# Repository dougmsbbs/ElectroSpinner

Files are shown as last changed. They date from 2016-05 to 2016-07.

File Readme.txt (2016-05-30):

   The Whirl-A-Rama is a open source electrospinning machine designed for anyone to be able to reproduce. It is made from commonly available materials at low cost.
   It is an entry into the 2016 HackaDay prize contest. You can view it here: https://hackaday.io/project/10599-electrospinning-machine
   For an introduction to electrospinning, this is a good start: https://en.wikipedia.org/wiki/Electrospinning More links are available from the HackaDay project page listed above.
   Any questions or comments, my email address is dougmsbbs@hotmail.com
   NOTE: ALL of the files associated with this project are in a state of flux right now. The project is being actively developed and things not only 'might' change, they 'will' change!

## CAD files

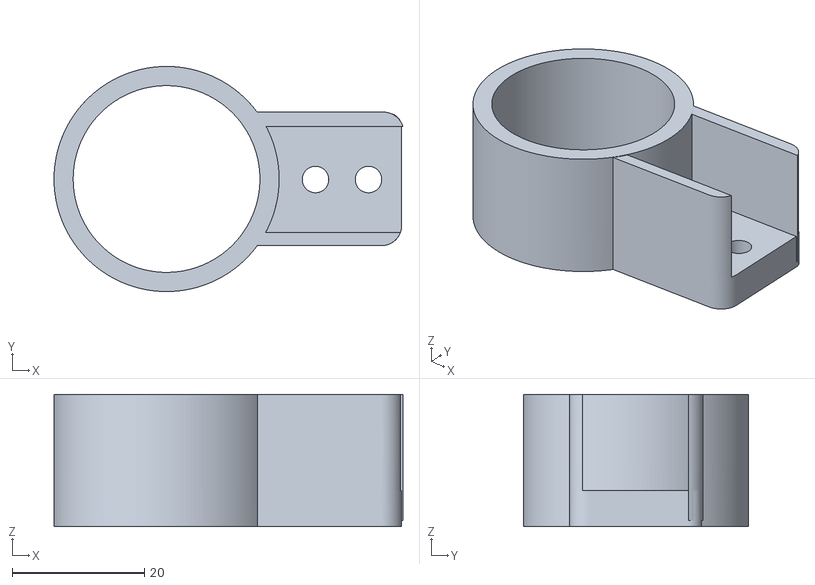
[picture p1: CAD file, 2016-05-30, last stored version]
Electrospinner/SwingHinge.stl
52.7 x 34.0 x 20.0

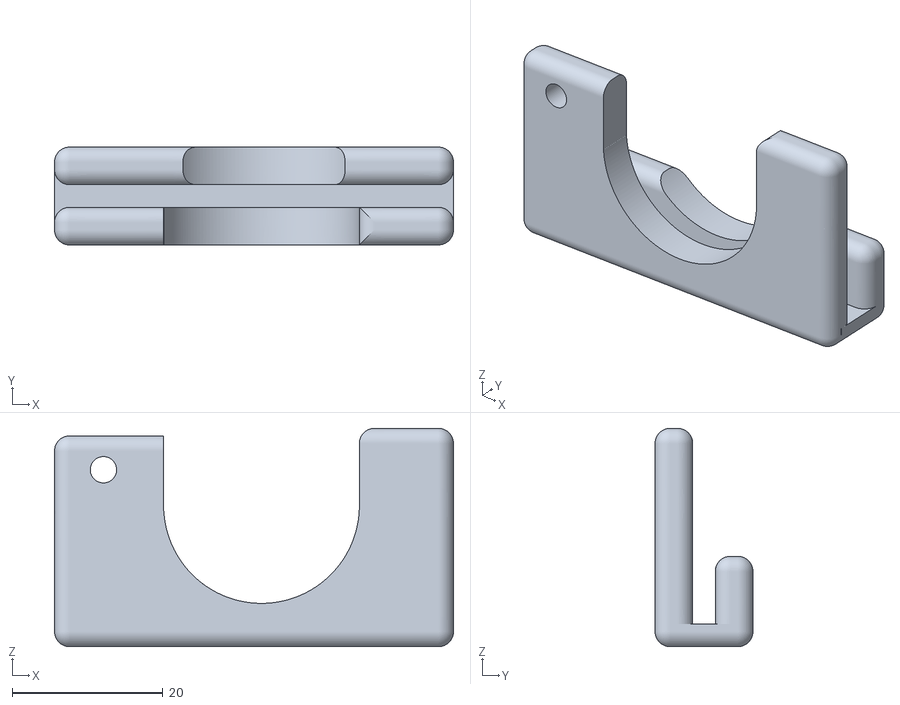
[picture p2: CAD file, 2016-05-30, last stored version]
Syringe/PlungerMountCap.stl
53.0 x 13.0 x 29.0

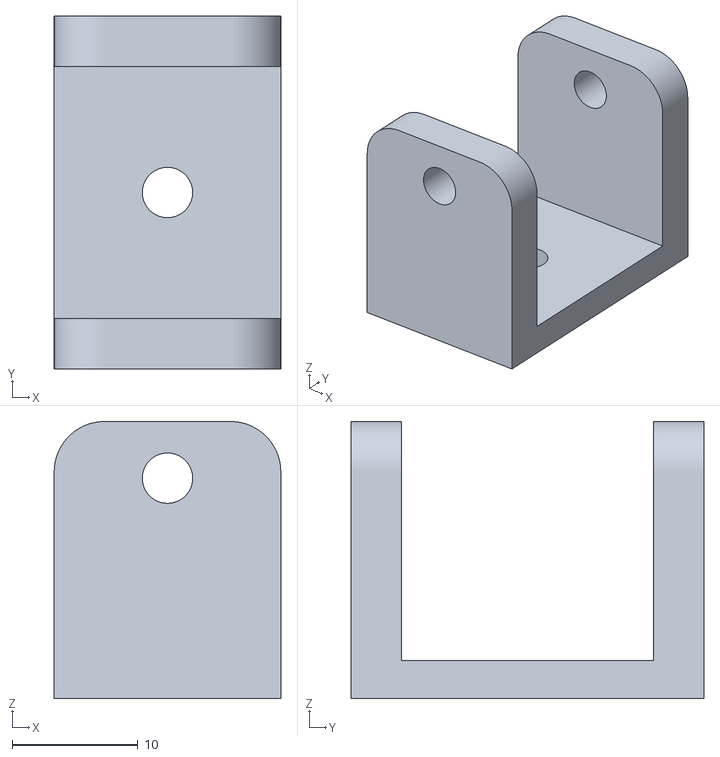
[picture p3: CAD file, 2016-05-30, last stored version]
Electrospinner/BottomIdlerBracket.stl
18.0 x 28.0 x 22.0

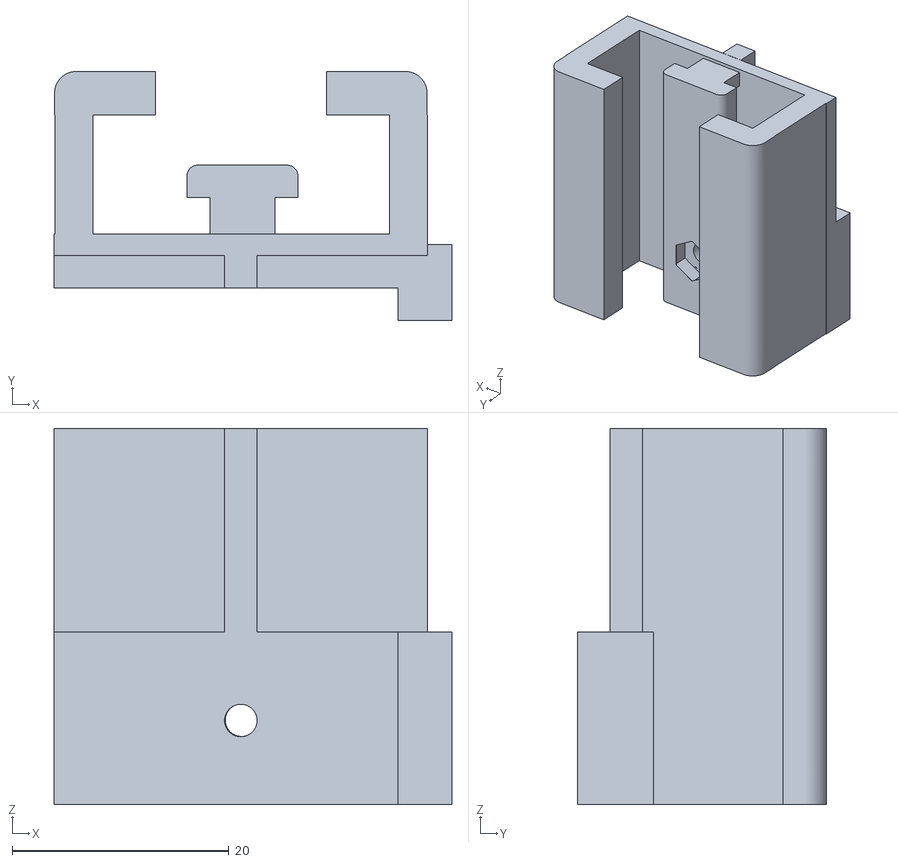
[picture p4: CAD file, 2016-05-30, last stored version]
Syringe/PlungerCarriageSlide.stl
36.8 x 23.0 x 34.7

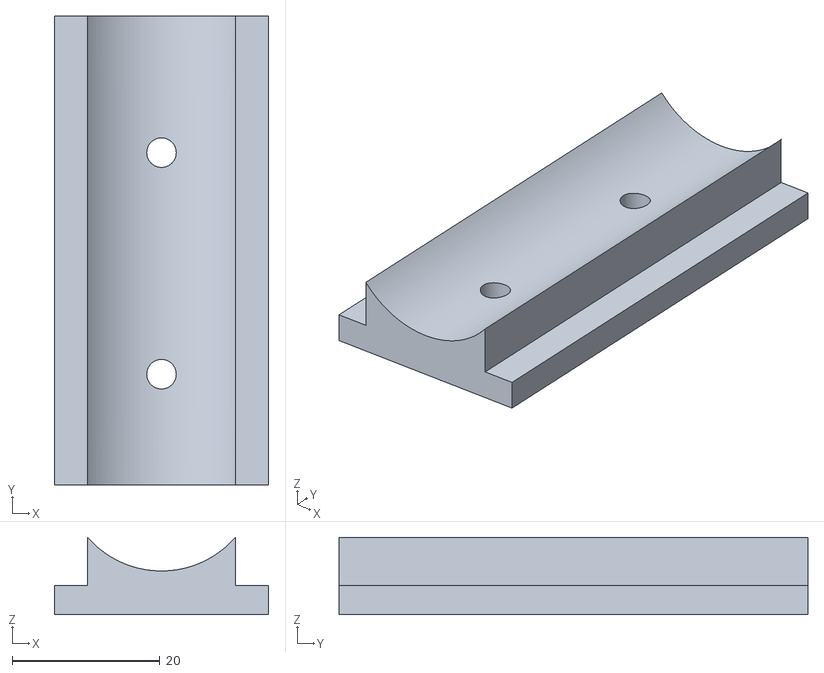
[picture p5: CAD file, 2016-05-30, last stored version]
Electrospinner/SideCoverBracket.stl
29.0 x 63.5 x 10.5

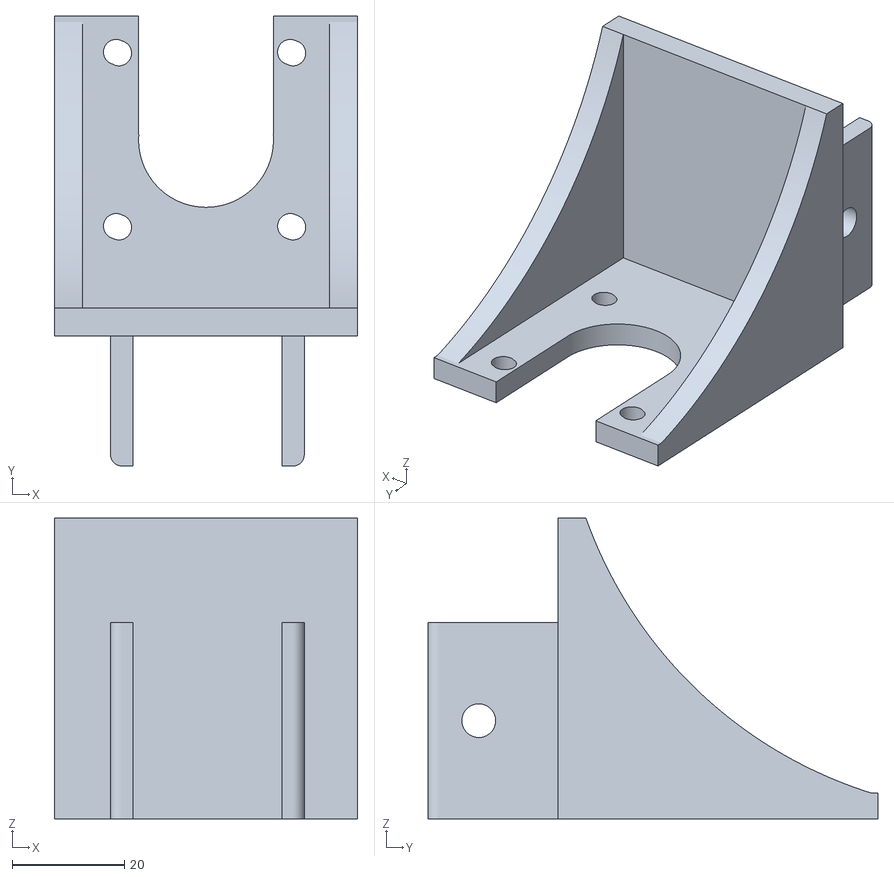
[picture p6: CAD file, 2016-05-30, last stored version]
Syringe/SyringeMotorMount.stl
54.0 x 80.1 x 53.6

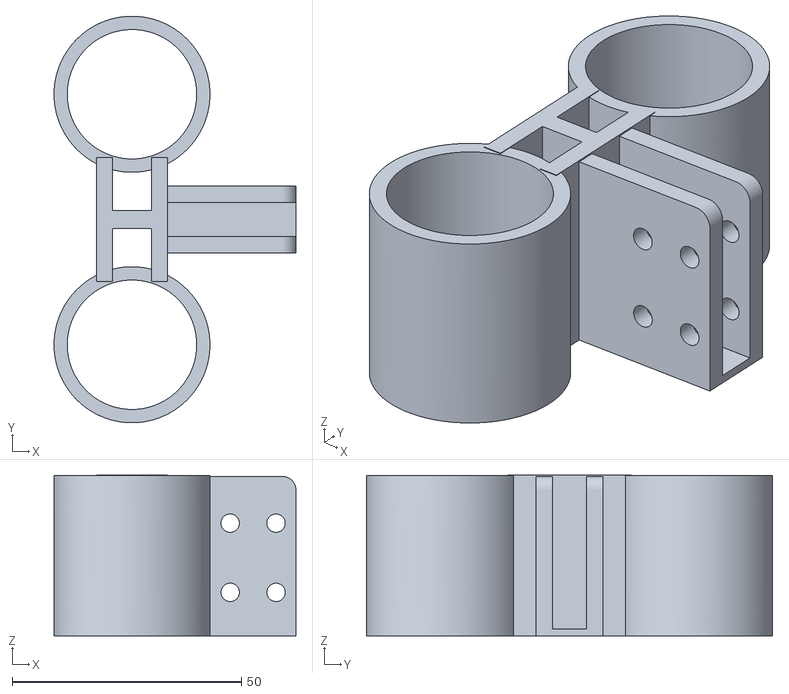
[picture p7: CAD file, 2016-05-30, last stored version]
Electrospinner/DoubleShaftCollar.stl
52.8 x 88.6 x 35.0

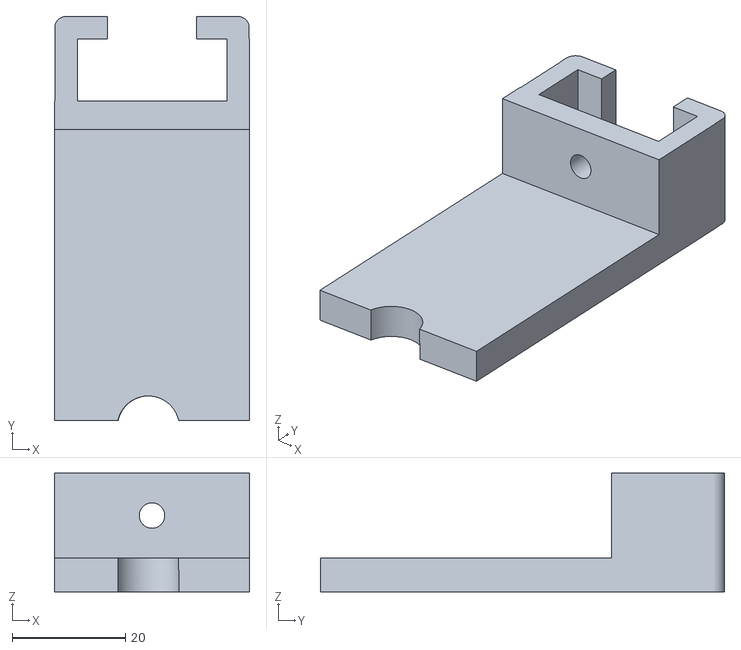
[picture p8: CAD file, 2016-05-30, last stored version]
Syringe/SyringeTipMount.stl
34.5 x 71.5 x 21.0

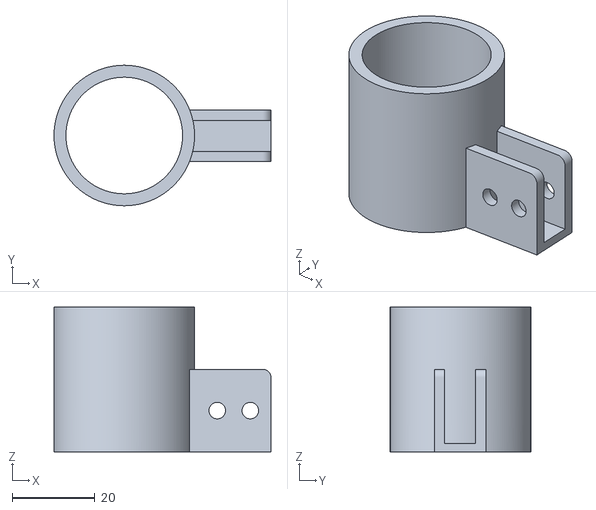
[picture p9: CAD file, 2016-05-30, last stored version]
Electrospinner/ShaftCollar.stl
52.5 x 34.0 x 35.0

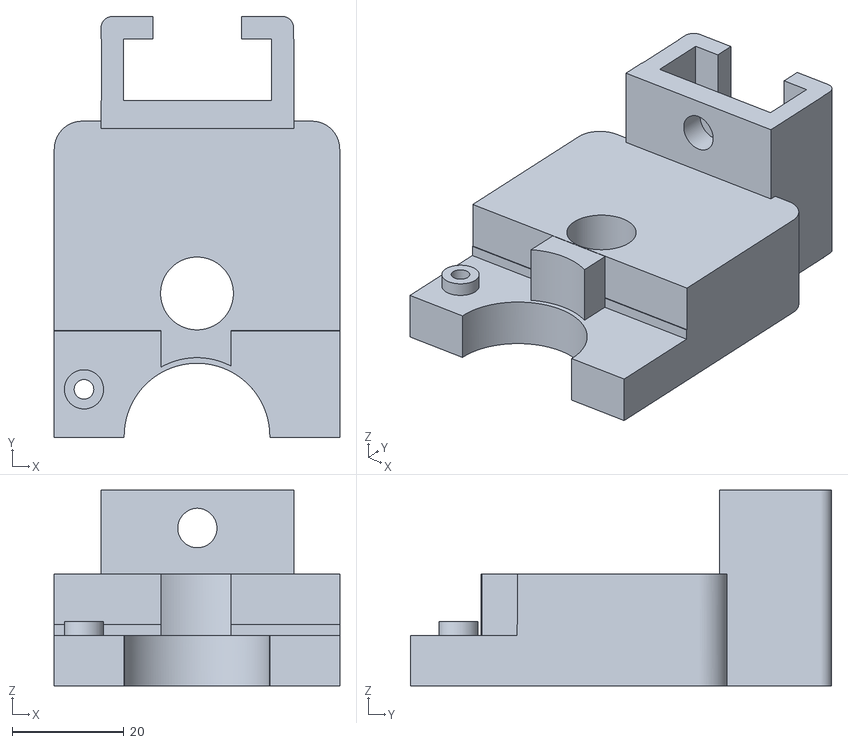
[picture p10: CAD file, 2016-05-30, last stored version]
Syringe/SyringeBodyMount.stl
51.0 x 75.2 x 35.0

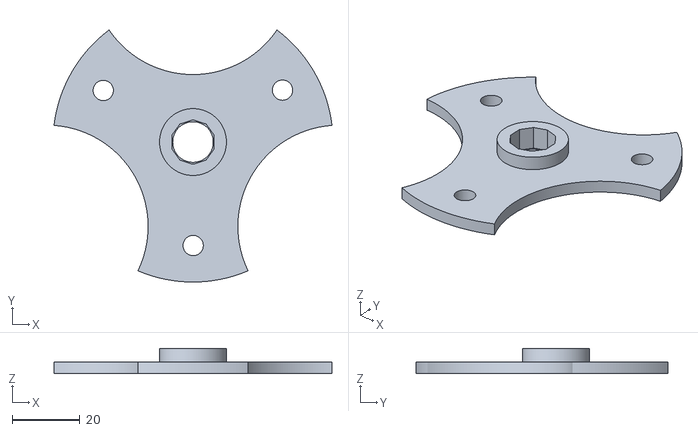
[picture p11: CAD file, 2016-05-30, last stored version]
Electrospinner/TopFittingMount.stl
82.3 x 74.7 x 7.48

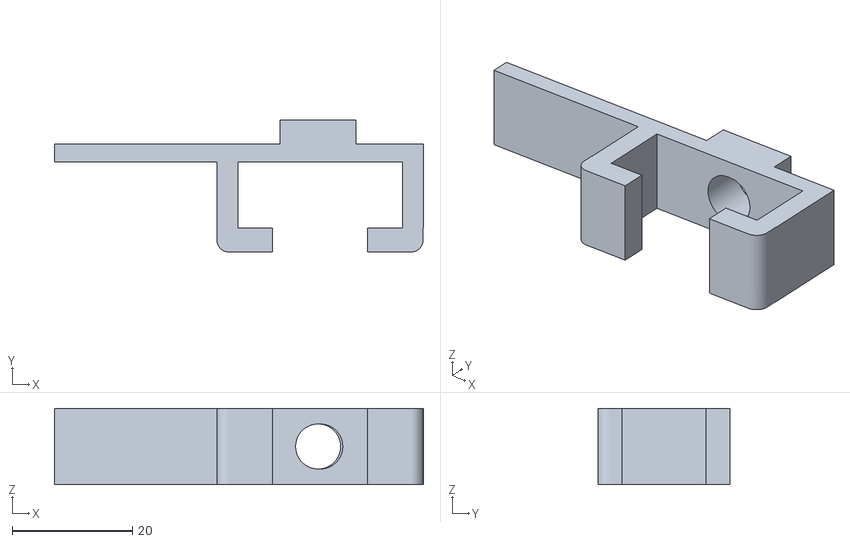
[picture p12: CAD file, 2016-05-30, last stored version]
Syringe/SwitchMount.stl
61.5 x 22.0 x 12.7

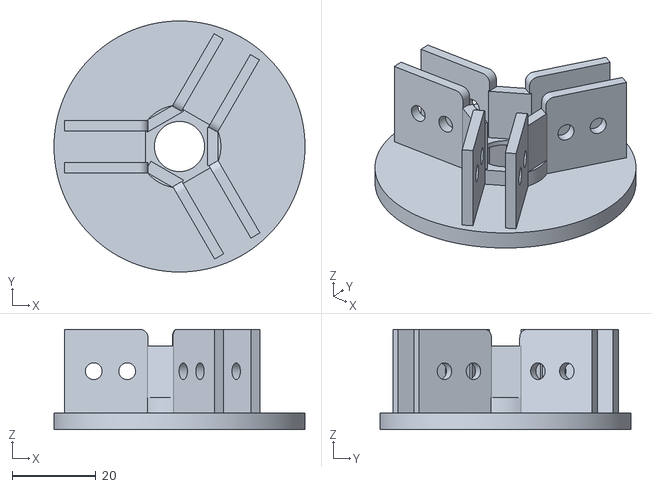
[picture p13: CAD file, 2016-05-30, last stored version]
Electrospinner/CenterHub.stl
60.0 x 60.0 x 24.0

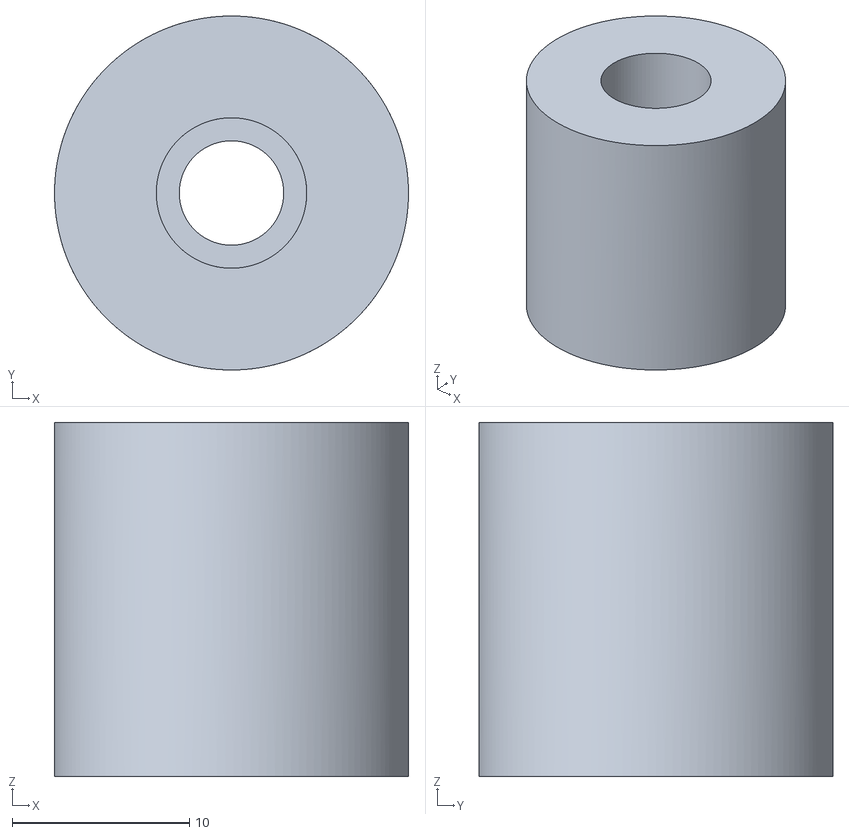
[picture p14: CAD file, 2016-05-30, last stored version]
Syringe/ShaftCoupler5-16.stl
20.0 x 20.0 x 20.0

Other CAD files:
Electrospinner/SwitchFlag.stl
Syringe/PlungerMount.stl
Electrospinner/DoorTrack.stl
Electrospinner/BeltClamps.stl
Electrospinner/BedLevelers.stl
Electrospinner/BottomIdlerBracketB.stl
Electrospinner/DoorEdging.stl
Electrospinner/DoorLatch.stl
Electrospinner/DoorLatchBase.stl
Electrospinner/LevelingBracket.stl
Electrospinner/Levelingcollar.stl
Electrospinner/LevelingcollarB.stl
Electrospinner/OutSideGuides.stl
Electrospinner/PlateLevelers.stl
Syringe/CarriageScrewHolder.stl
Syringe/PlungerMountThreadedRod.stl

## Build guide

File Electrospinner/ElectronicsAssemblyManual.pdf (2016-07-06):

# Electronics Assembly Manual

### for the

# ElectroSpinner - Whirl-A-Rama

Copyright 2016 by Douglas Miller

Licensed as Creative Commons Attribution-ShareAlike 3.0

Questions or corrections should be emailed to dougmsbbs@hotmail.com

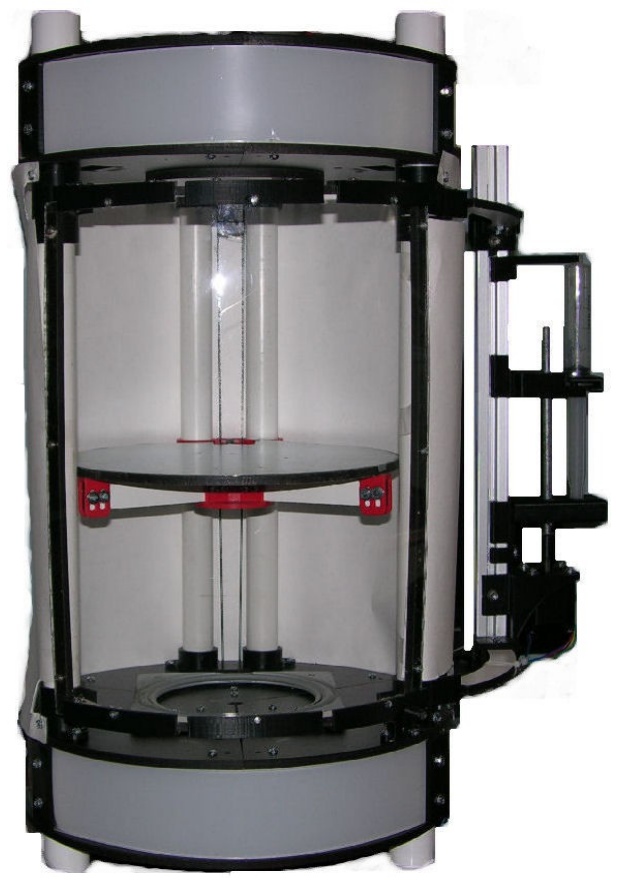
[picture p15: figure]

Note:
This machine can be operated with a variety of HV power supplies and syringes. For that reason, as well as my attempt to put as much information about the machine out as soon as I can, the construction manuals are divided up into individual components. The suggested building order is cabinet, syringe, HV power supply and finally the electronics.

All of the files for this project are available at the projects github page at https://github.com/dougmsbbs/ElectroSpinner.

Table of Contents

Note: | 2
Parts List | 4
3D Printed Parts: | 4
Purchased Items: | 4
Part Identification | 6
Prepare The gShield | 7
Mount The Terminal Strip | 7
Switch Wiring | 8
Power-In Wiring | 9
Arduino Power | 10
gShield Wiring | 11
Stepper Motor Wiring | 11
Top Limit Switch | 12
USB Cable | 12
HV Wiring | 13
Chamber Ground Wire | 14
Syringe Wiring | 14
We Need Power! | 15
Modifying an ATX Style Power Supply | 16
High Voltage Time! | 19
Uploading the Firmware | 20

### Parts List

3D Printed Parts:
Amount | Item
1 | Terminal Mount
1 | DoorSwitchMount

Purchased Items:
Note: Only items used in the manual are listed. Additional items needed to complete the project will be listed in those manuals (Assembly manual, Syringe manual.)
Amount | Part | Cost
1 | gShield Motor Controller | $50.00
1 | Power Supply 12v DC Output 29A | $50.00
| Enclosed Style
1 | 8 Pin Terminal Block | $2.75
1 | USB A-B Cable - 6 foot | $3.95
1 | Dual Row 5 Position Screw | $2.50
| Terminal Strip
1 | Limit Switch–Long Arm 2”(50.8mm) $5.38
| 15Amp. uxcell V-153-1C25
2 | M3x12mm Bolt
2 | M3 Nut
2 | M4x16mm Bolts
2 | M4 Nuts

2 | M2x16mm Bolts
2 | M2 Nuts
4 | M2 Washers
1 | 24” (610mm) 18awg wire | $1.00
| Duel Conductor.
24” | 18awg hookup wire. Red | $5.00
24” | 18awg hookup wire. Black $5.00
2 | 18awg Crimp Terminals- Female | $.20
2 | Alligator Clips – 1”(27mm) or larger $1.00
10'(3048mm) HV Wire – 40kV | $12.48
| This is enough for several machines.
6 | Wire Ties – Small | $.50
2 | Pair of Wire Bullet Connectors | $.50
| (two each – male and female)

Part Identification

### 3D Printed Parts:

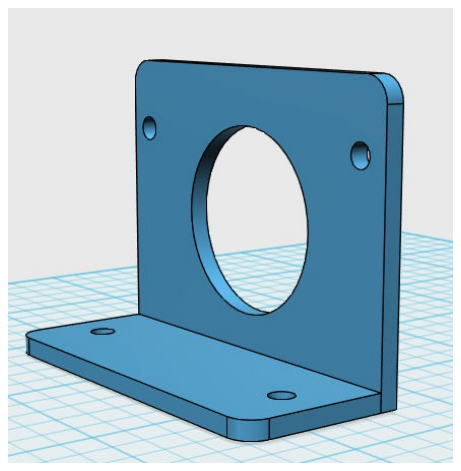
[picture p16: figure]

Prepare The gShield.

We're going to need to add a few header pins to the gShield before we mount it in the machine. In particular we need to bring out the D8 through D13 and Grd lines. We won't be using all of them, but we'll just add the entire row of pins while we're there, and we won't have to revisit this when we expand the machine in the future.
So go ahead and solder the 8 pin terminal block in place on the gShield.

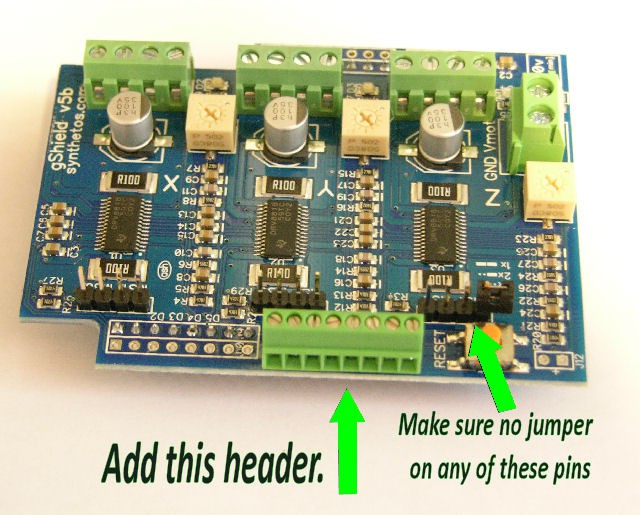
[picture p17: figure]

While you're looking at it, make sure none of the jumpers are on the MS1 MS0 pins on any of the axis's. We want micro-stepping on.

Mount The Terminal Strip

We're going to use a terminal strip to distribute power, so lets get that installed now.
Start by cutting one each of the jumpers. Cut each so that you have two pieces of each, one with two spades and one with three. Mount these on the terminal block, with the two spade red one on the lower right, and the three spade one on the bottom left.

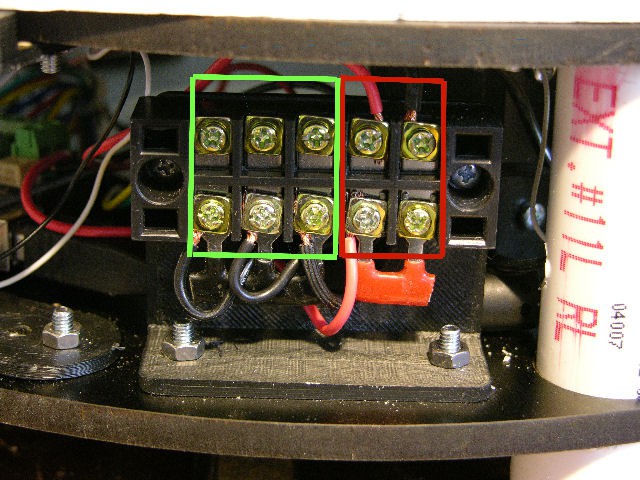
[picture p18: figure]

From now on all the positive wires we hook up will go on the four terminals within the red rectangle in the photo above. All the negative wires will go under terminals within the green rectangle.
Then mount it to the 3D printed TerminalMount. Use two M3x12mm bolts and nuts.
The assembly then gets mounted to plate B1DuelPost in the cabinet. It goes in the two holes between the posts and arduino. Use two M4x16 bolts and nuts, inserted up from the bottom. Refer to the photo above.

Switch Wiring

Next, install the microswitch with the long arm on it to the DoorSwitchMount 3D printed part. Use two M2x16mm bolts and nuts.
Now install the DoorSwitchMount by the slot in part B1DuelPost. Use two M2x16mm bolts, two M2 nuts, and four M2 washers. Adjust the switch in the slot until the switch is tripped when the door is in the closed position with the latch holding it in place.

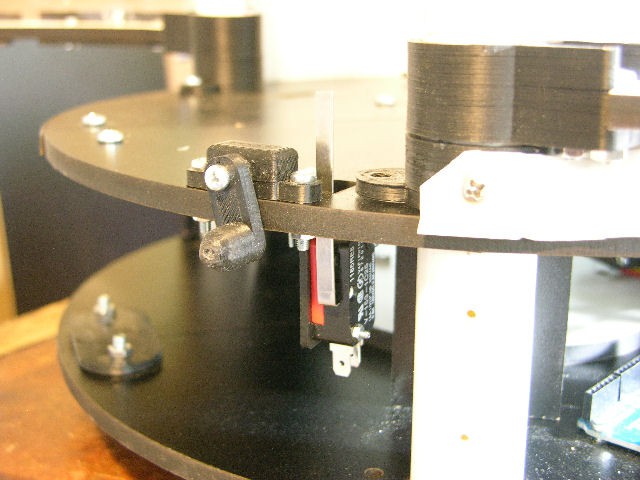
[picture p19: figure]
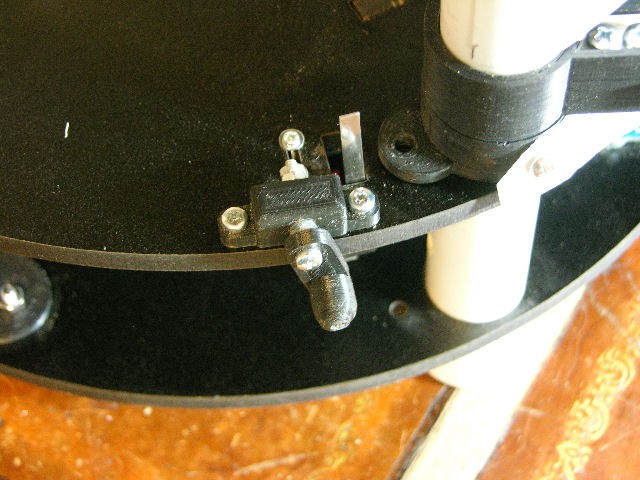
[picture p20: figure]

Power-In Wiring

Run the 24” (610mm) 18awg dual conductor wire in between the duel posts between decks B1 and B2. Route them so they come out from behind the terminal block, with the ground wire going to the black side, and the positive to the red side.
Like this:

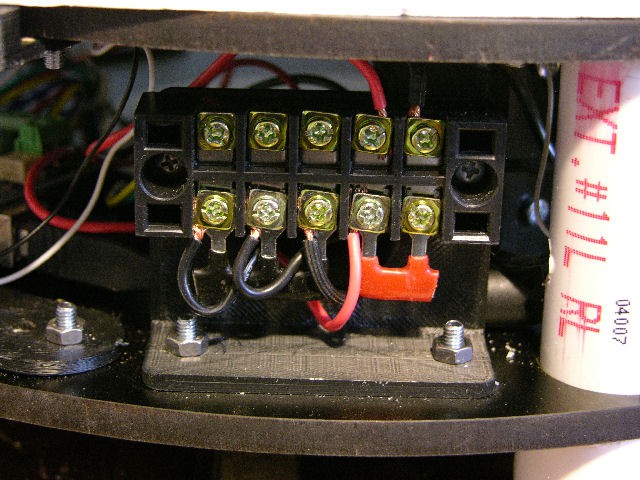
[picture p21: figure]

Fasten them both in place under the screws terminal.

Next, locate the two wires you ran up the right side rear post when you put the cabinet together. This will be the thicker wires coming out of the hole in the post.
These are the power going to our HV power supply, and they run all the way up and out the top of the machine.
Feed one of the wires (which is up to you, but if one has a stripe on it I'd use it for positive) into the back of the terminal block and out the front and fasten it to the negative strip. Fasten it down to the screw terminal.

The other of that pair of wires goes to the door switch center terminal. Install a female crimp terminal on the end of the wire and push it onto the switch.
Take another 12 inch (305mm) piece of 18awg wire and install a female crimp terminal on one end. Put that end on the normally open terminal on the door switch. Run the other end to the terminal block, insert it from the rear, and fasten it down to one of the positive screw terminals.
That's it for the power to the HV power supply. It will only come on when the door is closed.

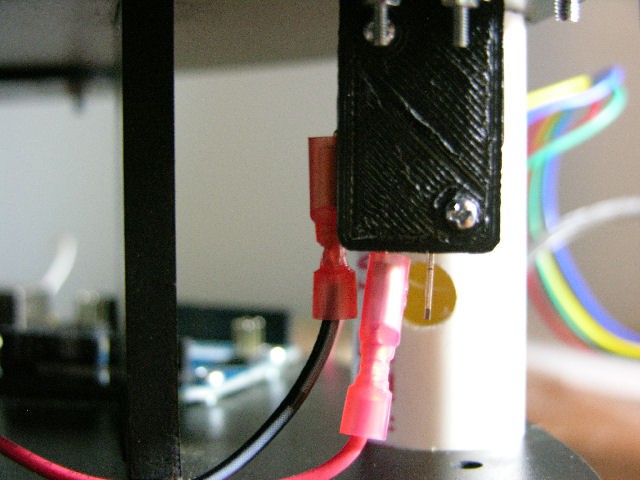
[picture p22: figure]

Arduino Power

Since we will be controlling the machine from the serial port connected to a computer, we don't need to power the arduino separately. So we can skip it. Go us!

gShield Wiring

The gShield does need power. So lets do that next.
Take two eight inch (203mm) lengths of the 18awg wire and fasten them to the next available screw terminal on the terminal block, black to negative, red to positive. Stay with our plan by sticking them in from the rear of the terminal block. Keeps everything all nice looking that way.
Lay the gShield on the table in front of the cabinet, with the two wires you just installed coming out from behind the terminal block. Fasten those wires to the gShield. Pay very close attention to the polarity as you install them. Make darn sure you have the red wire on positive and the ground on negative!
You can ruin the gShield if you get this wrong!
Be careful not to bend the pins on the gShield, but it's rather nice to be able to wire up the gShield outside of the cabinet. When it's all ready we'll mount it on the arduino.

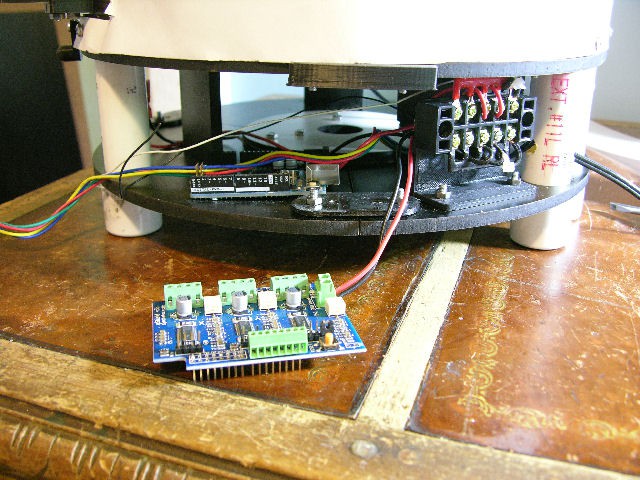
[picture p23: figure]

Stepper Motor Wiring

Time to wire up the stepper motor. Pull the wires from the stepper motor out, lay them beside the power wires going to the gShield, and trim them to about the same length.
Wire the four wires to the terminals for Z axis. If your stepper came with the wires in a plug-in connector wire them to the gShield in the same order. If there was no connector you'll have to find the order yourself. If you can't get that information from the manufacturer, there are plenty of web sites showing how to determine the order they need to go. Here I knew the order of mine was red, green, yellow, blue.

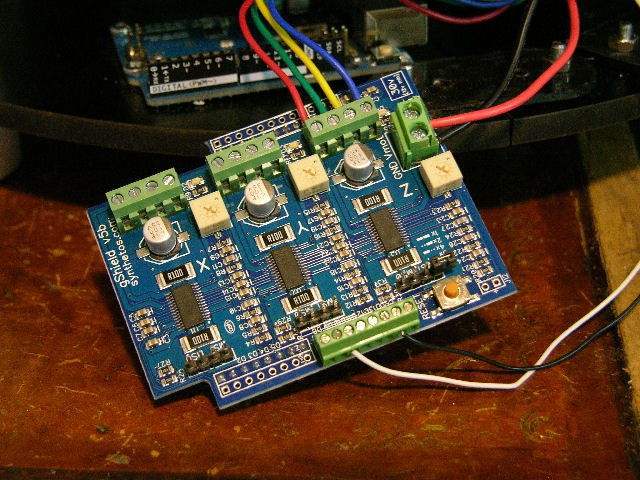
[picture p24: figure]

Top Limit Switch

Find the two signal wires you ran up inside of the rear post and fastened to the top limit switch. Run them behind the terminal block and out to the gShield.
Fasten one of the wires to the header screw terminal's you soldiered to the gShield way back at the start. It goes on pin 10. Wire the other one to the ground pin on the header. If you're not sure what the pin numbers are hold the gShield in place over the arduino, and it's printed on the side of the arduino header.
Pin ten should be the third pin from the left on that header, and ground is the second from the right.

USB Cable

Slide the USB cable in between the rear posts, behind the terminal block, and into the arduino.

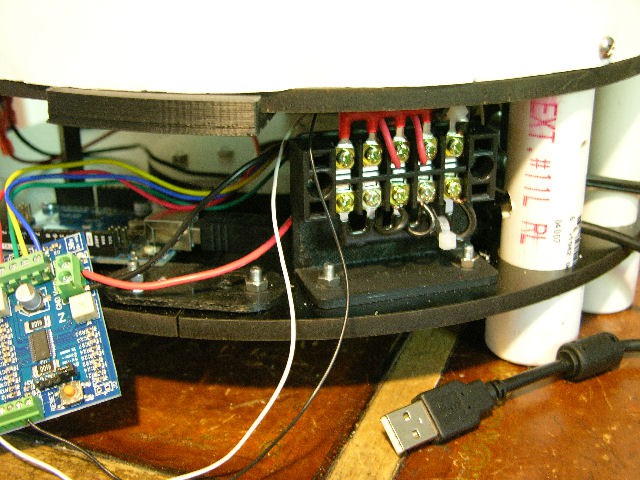
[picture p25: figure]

HV Wiring

Cut a piece of the HV wire to a length of twenty inches (508mm) and insert it down through the hole on the right side of piece T2DuelPost. See the picture below to locate the hole. Then feed it down through the matching hole in T1DuelPost and into the work chamber. Feed enough down so that you can comfortably reach it to attach an alligator clip.
Crimp one of the alligator clips onto the end in the chamber, then soldier it in place. Seeing how important this connection is to the functioning of the machine, it's best to both crimp and soldier it. Then hold the alligator clip up to the center of the chamber right below the hole in the center. Pull any excess back up on top of the machine.
Leave the extra on top alone for a bit. We'll fasten that to the HV power supply when we get that far.

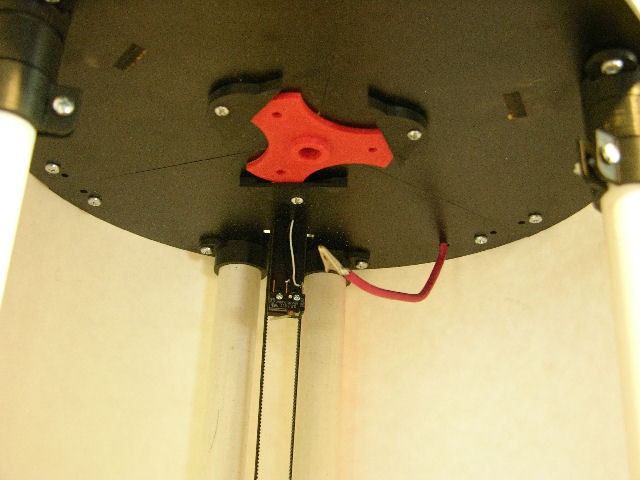
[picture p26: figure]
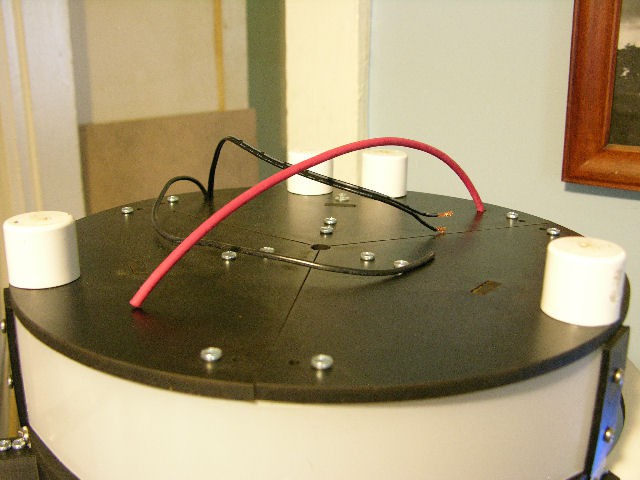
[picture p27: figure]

Chamber Ground Wire.

Attach another alligator clip to the ground wire that's coming up through the center hole in the bottom of the chamber. Same as above, crimp and then soldier in place.
This wire will be attached to the collecting plate when we run the machine.

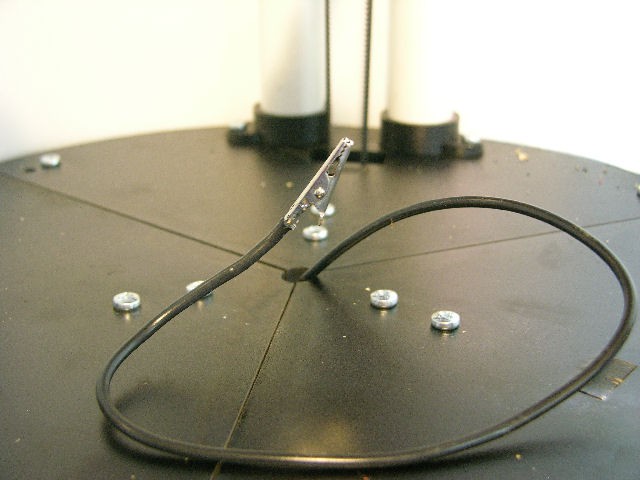
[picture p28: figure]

Syringe Wiring

Assuming you have already built the syringe for this project, or you have another one from a different source you would like to use, it's time to get it hooked up.
Any syringe pump that operates off of a four lead nema17 stepper motor should work just fine.
Start by routing the wires from the syringe pump into the cabinet. Wire tie the wires up neatly on the run from the stepper motor and along the lower swing arm. Then run them under the machine and up into the hole between the arduino and the front right post. Wire tie in enough places to keep the wires under control and looking neat. I like to add one just inside the cabinet where they enter and leave a little tail on it, to prevent the wires from getting pulled out.
Pull the gShield off of the arduino if you have it sitting on it, and pull it out of the cabinet a bit.
Wire the four stepper wires to the Y axis on the gShield. The order they go depends on the stepper motors you have. Check the manufacturers web site, or search the web to find out how to determine the correct order for your stepper motor.
Wire one of the wires coming from the syringe pumps limit switch to pin nine on the gShield header we soldered in place.
Connect the other wire coming from the limit switch to the ground terminal on the gShield right along with the cabinets limit switch ground.

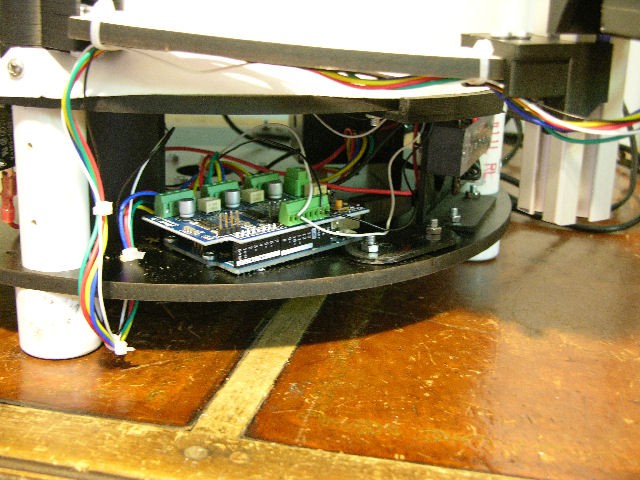
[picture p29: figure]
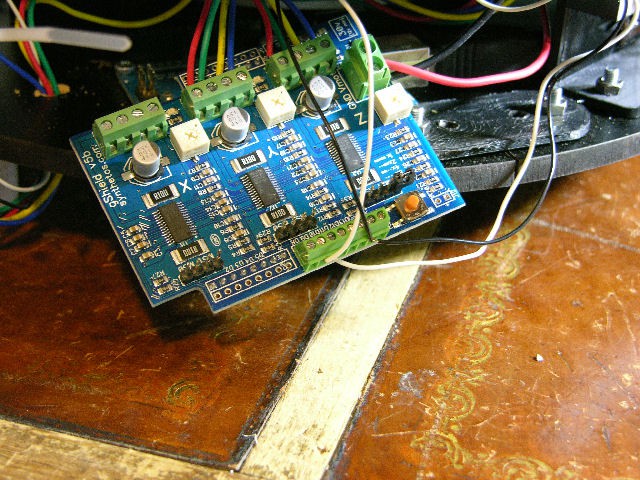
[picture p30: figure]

Carefully aligning the pins, place the gShield back onto the arduino and press down into place.

We Need Power!

You have several choices for a power supply. An ATX computer power supply is a popular choice, but takes a bit of work to get it ready. An enclosed type power supply is pretty much ready to go right out of the box.
The choice is yours. If you want my opinion, I'd say if you're spending money to buy a new supply, go for the enclosed one and avoid the extra work.

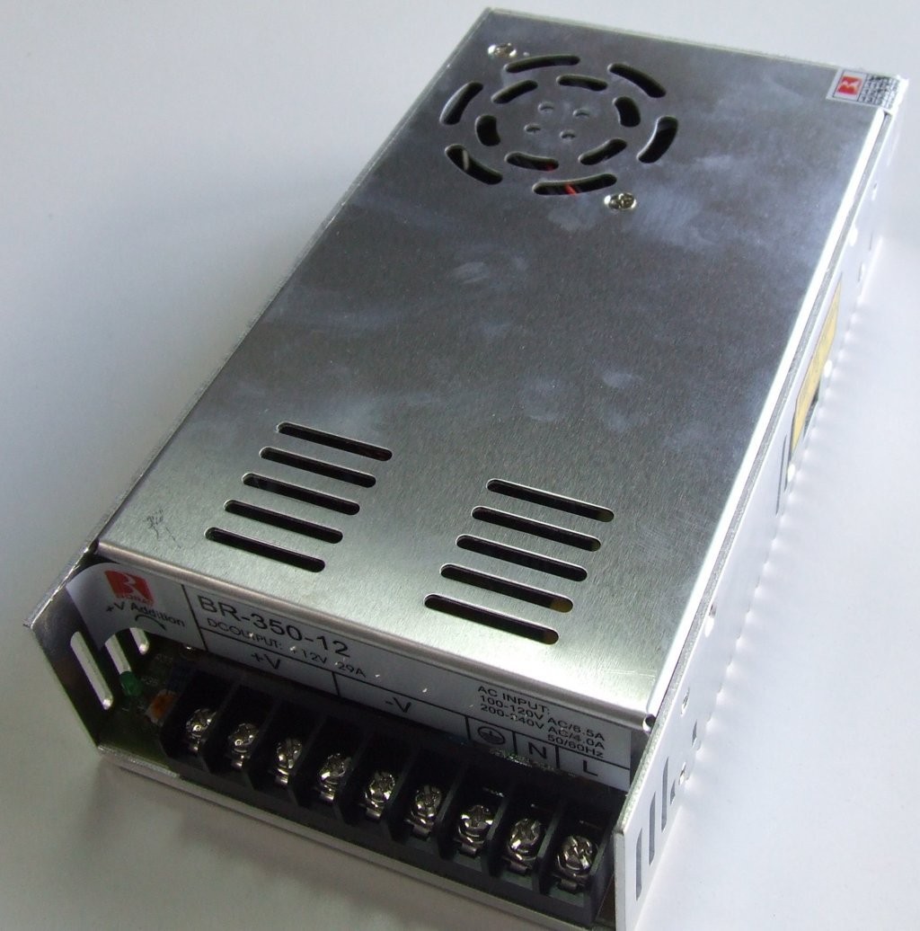
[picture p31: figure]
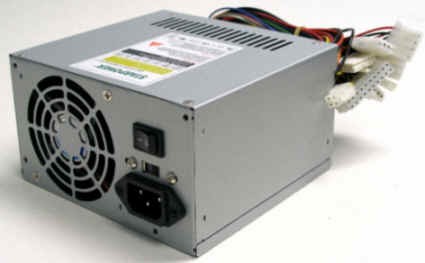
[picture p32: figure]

ATX Power Supply | Enclosed Power Supply

If you have the enclosed style, skip this next section and go right to wiring it up.

Modifying an ATX Style Power Supply

We need to make sense of that tangle of wires coming out the back of the power supply.
Start by taking the screws out of the top of the case. There is normally only four of them.
Take the top off and swing it off to aside. Most of them have a fan in the top piece, and you'll need to be sure and leave those wires intact.
Now find the wires you want to save. You need four of the yellow wires and five of the black ones. You also need the green wire.
Pull the ones you want to save off to one side, and cut all the others wires off.

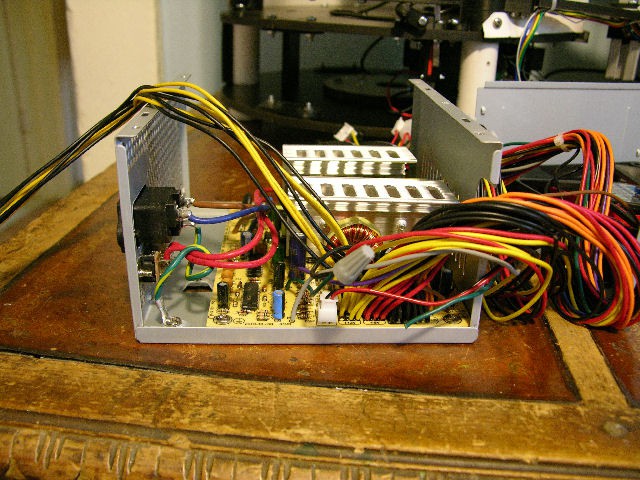
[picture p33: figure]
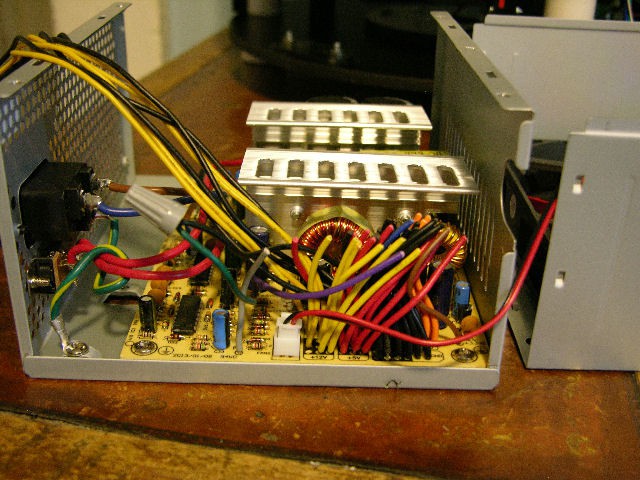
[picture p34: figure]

Tie the green wire and one of the black wires together with a twist on wire connector. That's the 'power good' signal that will let the power supply come on.
Take the four yellow and four black wires you pulled aside and trim them down to the same length, leaving them as long as you can. Strip the ends off and twist them together, all black in one bundle, all yellow in the other.
Install a female bullet connector on the yellow wires, and a male on the black wires. That way you can disconnect the power supply from the cabinet, and still be sure to plug them back in correctly.
Now we need to install the bullet connectors on the 24” duel conductor wire. This time you will put the male connector on the wire that will be our positive lead, and the female on the ground wires.
Leave this unplugged for the moment. We'll want to test the supply first.

Pull that duel conductor wire out the rubber grommet in the power supply's case, and wire tie it so it can't get pulled out the back. My power supply had a loop in the rubber grommet just perfect to hold the wire tie in place, so I used that. If yours has no such thing put two wire ties on, pointed in opposite directions, and don't trim them down all that much. See if that will keep them from being pulled out. Whatever you come up with that works, great. As long as they can't be yanked out of the supply, it's all good. Yours should look something like this:

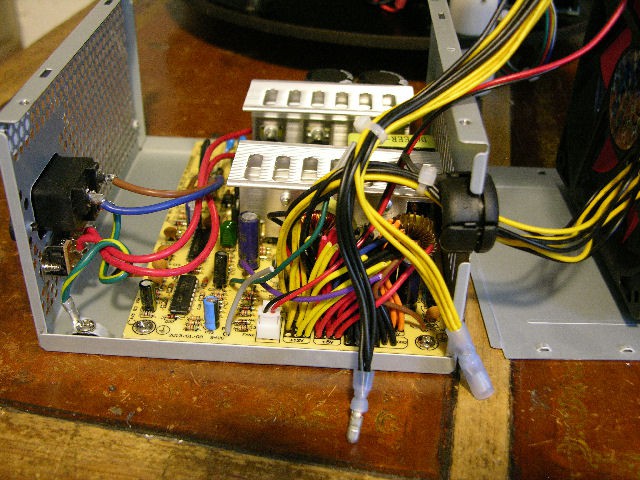
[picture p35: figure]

Put the cover back on the power supply and install all four screws.

It's time to test it out. Hook up a meter to the output wires, and plug in the power supply. The fan on the power supply should come on and the meter should read around 12 volts. If yours does, great!
If the fan does not come on and you get no voltage reading at all, it's most likely a problem with that 'power good' line. Unplug the supply and open it back up to see what's going on.
If the fan works but you get something other than 12 volts, you likely used the wrong wires. It would be a rare thing to not have the 12 volt being on the yellow wires (I've never seen it), but I guess it could happen.

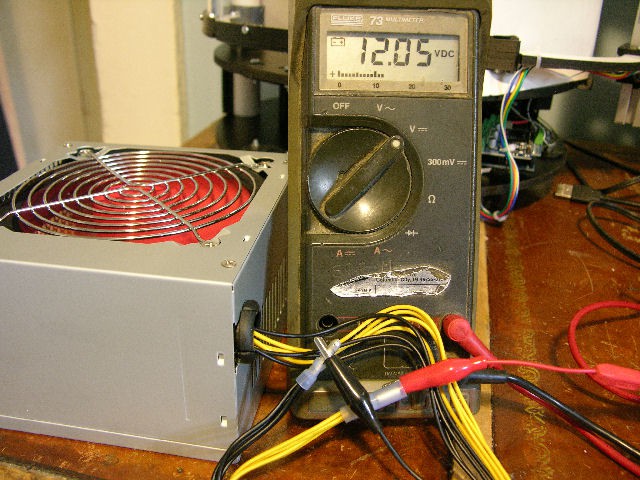
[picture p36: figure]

Given that you have the 12 volt output, unplug the power supply, and plug in the wires coming from the back of the cabinet. They're the ones with the matching bullet connectors we installed above.
Now double and even triple check that the polarity is correct by checking for continuity between the bullet connectors and the terminal block in the cabinet. Make sure that the 12 volt line coming out of the power supply is hooked to the 'red' section on the terminal block, and the ground from the power supply is connected to the 'black' terminal block section.
Incorrect polarity can destroy the gShield. Make darn sure it's correct!
One more little detail to take care of before we move on. Those wires going up to the top of the cabinet to power the HV supply are hanging in the wind up there. If they were to touch each other it wouldn't be a good thing. Make sure they are separated, or better yet put a wire cap on them. Just taping them off would work too.
If all is well, you're ready to test it out. With the bullet connectors firmly together, plug in the power supply. You should see the blue LED glow on the gShield.
Ain't that a grand sight!
If you see the light (pun intended), move your meter to the two leads on top of the machine. Plug the power supply in. Open and close the door a few times to make sure it's working okay. You should get 12 volts when the door is closed, and zero volts when it's open.
If there is a problem with any of that, unplug the supply and track the wiring back until you find the problem. It's in there somewhere. And you'll find it in short order, I'm sure.

At this stage, you can replace the side covers on the cabinet. With all that working, the only thing missing as far as wiring goes is the HV power supply.
We'll get to that next.

High Voltage Time!

Assuming you have the high voltage supply sitting there staring at you, we can wire it up now.
The HV supply for this project works well, but it's not your only option. If you have another one, feel free to use it. It needs to be powered by 12 volts, but that's about all you need to worry about. Whatever you use should have an adjustable output, and go

up to 30kV.
The HV supply sits on top of the machine, where's it close to the nozzle, giving us as short a HV voltage path as we can get. So go ahead and place it up there.
Wire the two 12 volt leads up to the input of your HV supply, paying close attention to the polarity.
The ground output from the HV supply goes to the ground wire running down the left duel post.
The high voltage output goes to the HV wire going down the small hole on the right side, and leads to the alligator clip hanging at the top inside the cabinet.

That's it for the wiring.
All you need now is the firmware uploaded to the arduino.

Uploading the Firmware

To upload the firmware you will need the arduino IDE, the firmware for the electrospinner, as well as the library AccelStepper.
The arduino IDE can be downloaded here: https://www.arduino.cc/en/Main/Software
The electrospinner software is available on the projects github page: https://github.com/dougmsbbs/ElectroSpinner.
And finally, the AccelStepper library can be found here: http://www.airspayce.com/mikem/arduino/AccelStepper/AccelStepper-1.51.zip1 (http://www.airspayce.com/mikem/arduino/AccelStepper/AccelStepper-1.51.zip1)

Follow the directions to install the arduino IDE. Then install the AccelStepper library. Instructions to do both are included in the IDE download, or can be found all over the web.
Plug the USB cable coming from the electrospinner into your computer. Load up the electrospinner firmware in the arduino IDE, and tell it to compile and upload. When it's done uploading, you can use the arduino IDE's serial monitor screen to send commands that will run the electrospinner. Instructions on the best techniques and all the commands will be in the Operations Manual (as of 7/7/2016 not yet completed). Keep checking the projects github page to see when it's ready for release.

Also in the works is a windows 8.1 or greater GUI for the electrospinner. It will also be released on the projects github page.

That's about it. Your machine is put together and ready for a run. The how's and why's of that will be in the Operations Manual when it's ready for release. There is a lot to try with this machine, and I'm sure I won't be the one to discover all of them. I look forward to any and all knowledge you gain from using this machine, and sharing it with the rest of us.

It's going to be an interesting few years, while we explore all that is possible with a hobby level electrospinning machine about anyone can build. I can't wait to see what you come up with!

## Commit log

2016-05-30 Electrospinner
    Open source electrospinning machine.
    [CarriageScrewHolder.stl, PlungerCarriageSlide.stl, PlungerMount.stl, PlungerMountCap.stl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]
2016-05-30 Electrospinner Cabinet Files.
    [BedLevelers.stl, BeltClamps.stl, BottomIdlerBracket.stl, BottomIdlerBracketB.stl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]
2016-06-25 Updated Files
    Updated and organized all files for the cabinet.
    [BedLevelers.stl, BeltClamps.stl, BottomIdlerBracket.stl, BottomIdlerBracketB.stl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]
2016-07-01 Files changed.
    Changed files B1DuelPost and B2Right.
    Added DoorSwitchMount STL.
    Changed assembly guide to reflect new files.
2016-07-05 More file changes
    Changed a few files. Added Syringe assembly manual.
    [CarriageScrewHolder.stl, PlungerCarriageSlide.stl, PlungerMount.stl, PlungerMountCap.stl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]
